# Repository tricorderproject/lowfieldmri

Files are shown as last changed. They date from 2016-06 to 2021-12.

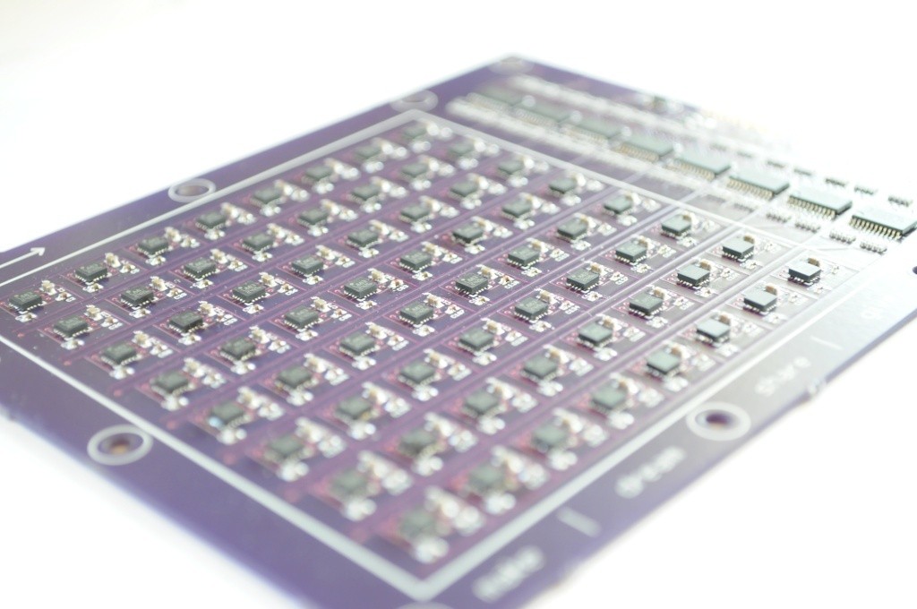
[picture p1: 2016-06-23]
hardware/magarray_v1/assembled_board1.jpg

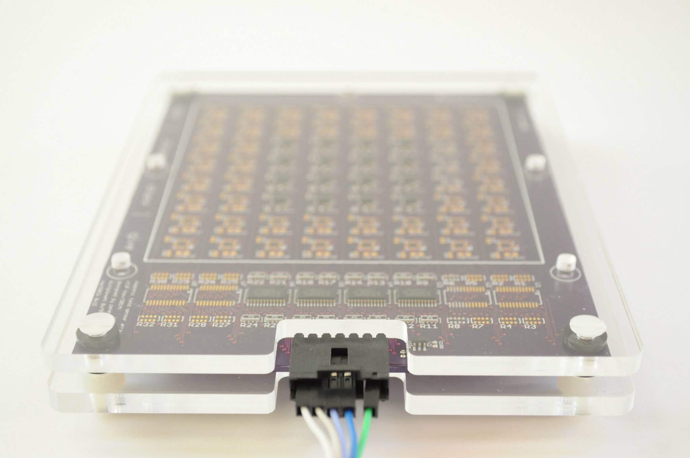
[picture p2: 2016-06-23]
hardware/magarray_v1/assembled_board2.jpg

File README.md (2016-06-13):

lowfieldmri
======

Experiments in Earth's field magnetic resonance imaging<br>

**DISCLAIMER OF WARRANTIES AND LIMITATION OF LIABILITY.**

UNLESS OTHERWISE SEPARATELY UNDERTAKEN BY THE LICENSOR, TO THE MAXIMUM EXTENT POSSIBLE, THE LICENSOR OFFERS THE LICENSED MATERIAL AS-IS AND AS-AVAILABLE, AND MAKES NO REPRESENTATIONS OR WARRANTIES OF ANY KIND CONCERNING THE LICENSED MATERIAL, WHETHER EXPRESS, IMPLIED, STATUTORY, OR OTHER. THIS INCLUDES, WITHOUT LIMITATION, WARRANTIES OF TITLE, MERCHANTABILITY, FITNESS FOR A PARTICULAR PURPOSE, NON-INFRINGEMENT, ABSENCE OF LATENT OR OTHER DEFECTS, ACCURACY, SAFETY, OR THE PRESENCE OR ABSENCE OF ERRORS, WHETHER OR NOT KNOWN OR DISCOVERABLE. WHERE DISCLAIMERS OF WARRANTIES ARE NOT ALLOWED IN FULL OR IN PART, THIS DISCLAIMER MAY NOT APPLY TO YOU.

TO THE EXTENT POSSIBLE, IN NO EVENT WILL THE LICENSOR BE LIABLE TO YOU ON ANY LEGAL THEORY (INCLUDING, WITHOUT LIMITATION, NEGLIGENCE) OR OTHERWISE FOR ANY DIRECT, SPECIAL, INDIRECT, INCIDENTAL, CONSEQUENTIAL, PUNITIVE, EXEMPLARY, OR OTHER LOSSES, COSTS, EXPENSES, OR DAMAGES ARISING OUT OF THIS PUBLIC LICENSE OR USE OF THE LICENSED MATERIAL, EVEN IF THE LICENSOR HAS BEEN ADVISED OF THE POSSIBILITY OF SUCH LOSSES, COSTS, EXPENSES, OR DAMAGES. WHERE A LIMITATION OF LIABILITY IS NOT ALLOWED IN FULL OR IN PART, THIS LIMITATION MAY NOT APPLY TO YOU.

THE DISCLAIMER OF WARRANTIES AND LIMITATION OF LIABILITY PROVIDED ABOVE SHALL BE INTERPRETED IN A MANNER THAT, TO THE EXTENT POSSIBLE, MOST CLOSELY APPROXIMATES AN ABSOLUTE DISCLAIMER AND WAIVER OF ALL LIABILITY.

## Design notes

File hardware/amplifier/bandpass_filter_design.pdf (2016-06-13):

## FilterPro Design Report

## Schematic

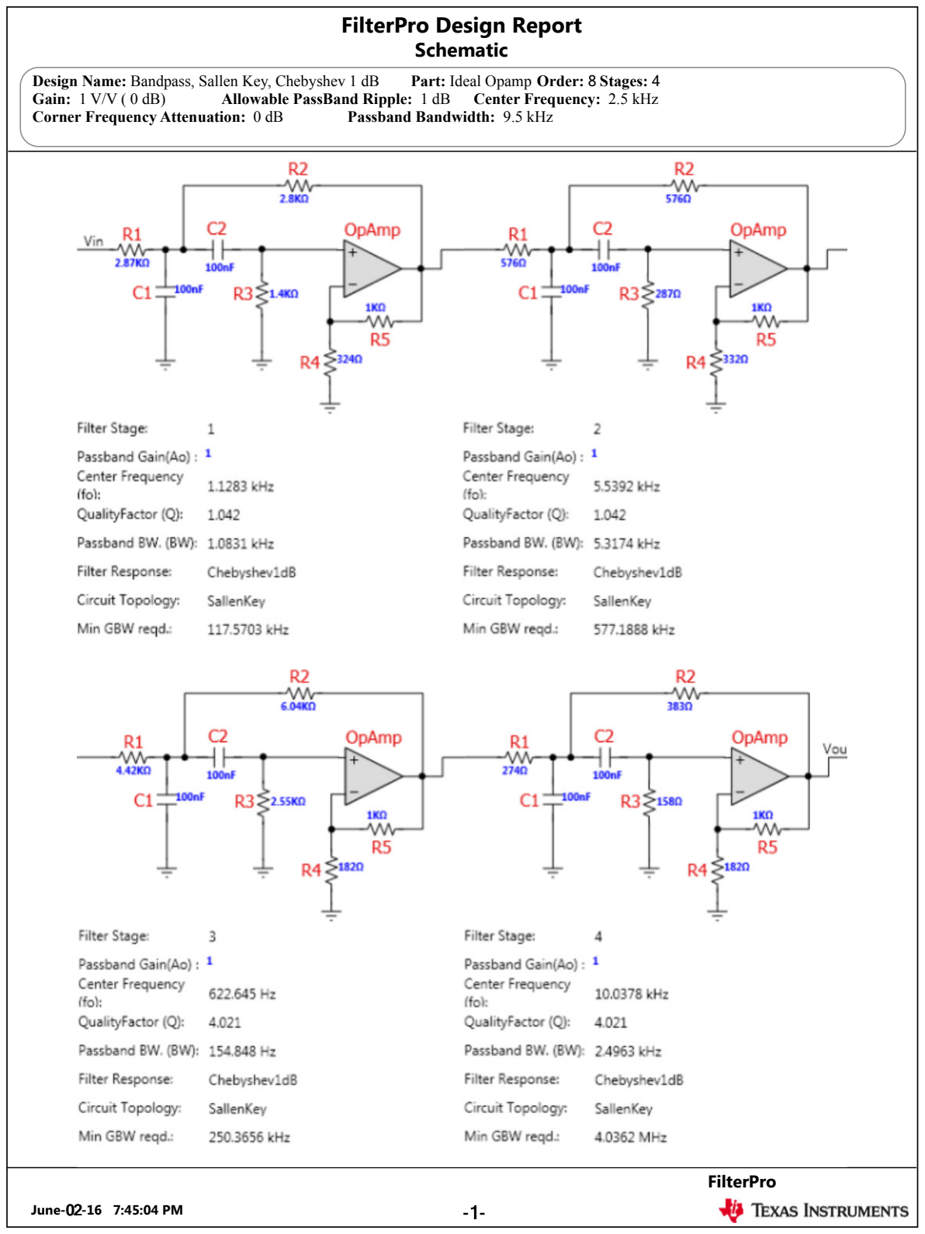
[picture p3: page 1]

Design Name: Bandpass, Sallen Key, Chebyshev 1 dB | Part: Ideal Opamp Order: 8 Stages: 4
Gain: 1 V/V ( 0 dB) | Allowable PassBand Ripple: 1 dB | Center Frequency: 2.5 kHz
Corner Frequency Attenuation: 0 dB | Passband Bandwidth: 9.5 kHz
June-02-16 7:45:04 PM | -1-

## FilterPro

## Frequency and Phase Responses

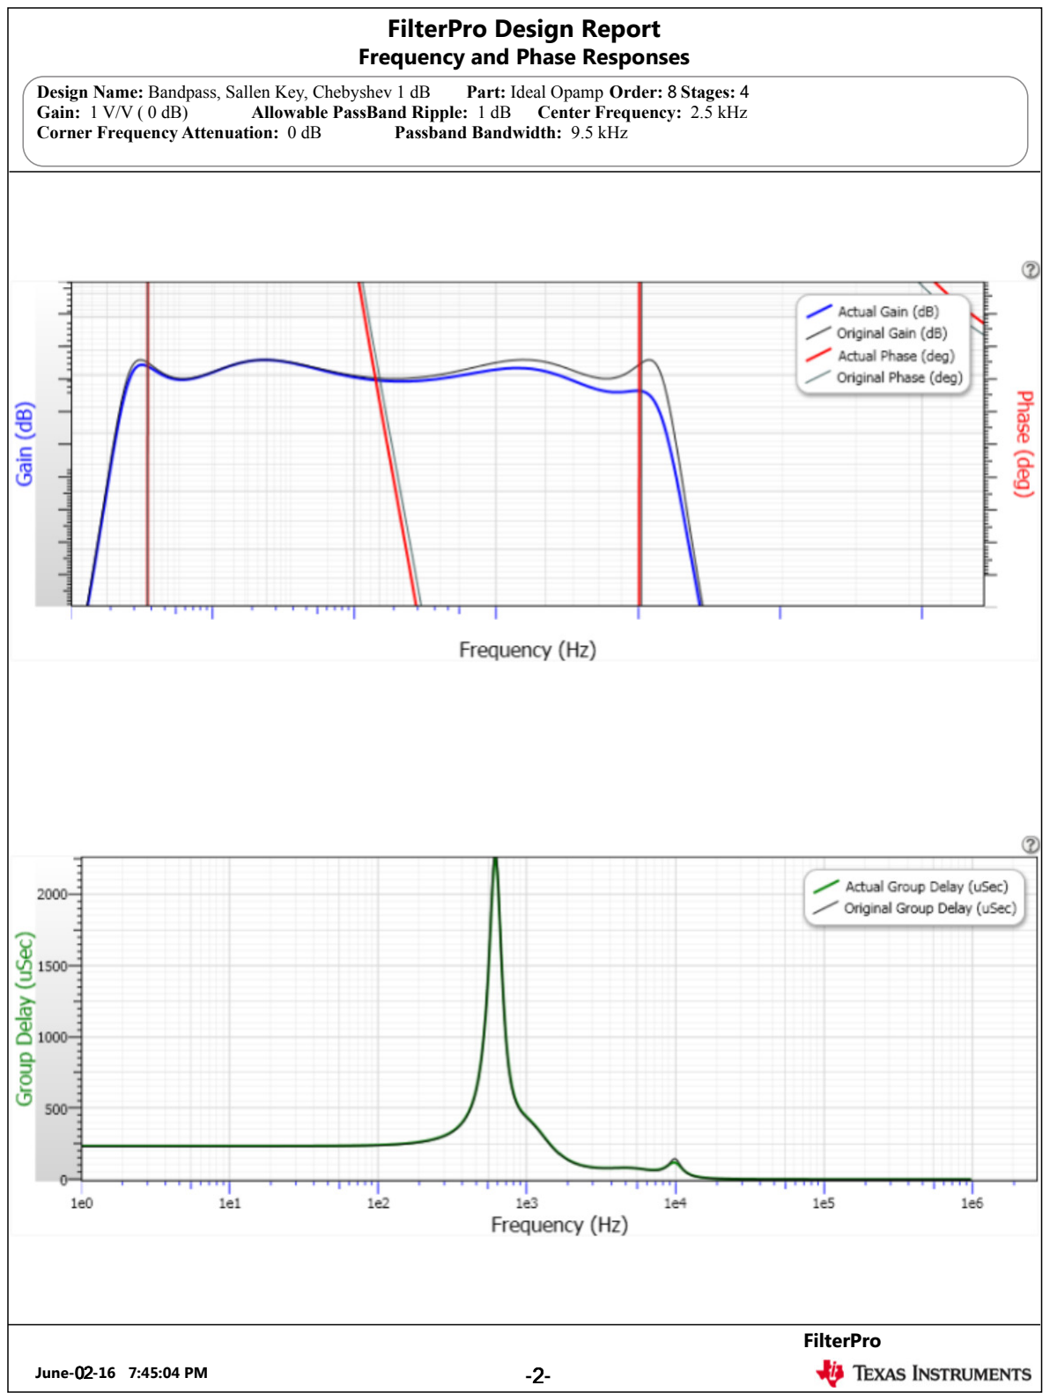
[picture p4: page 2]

Gain: 1 V/V ( 0 dB) | Allowable PassBand Ripple: 1 dB | Center Frequency: 2.5 kHz
Corner Frequency Attenuation: 0 dB | Passband Bandwidth: 9.5 kHz
June-02-16 7:45:04 PM | -2-

Gain: 1 V/V ( 0 dB) | Allowable PassBand Ripple: 1 dB | Center Frequency: 2.5 kHz
Corner Frequency Attenuation: 0 dB | Passband Bandwidth: 9.5 kHz

## Bill of Materials

June-02-16 7:45:04 PM | -3-
Element ID | Quantity | Part Number | Value | Tolerance | Description | Manufacturer
R1 (Stage 1) | 1 | Standard | 2.87KΩ | E96: 1% | Resistor
R2 (Stage 1) | 1 | Standard | 2.8KΩ | E96: 1% | Resistor
R3 (Stage 1) | 1 | Standard | 1.4KΩ | E96: 1% | Resistor
C1 (Stage 1) | 1 | Standard | 100nF | E96: 1% | Capacitor
C2 (Stage 1) | 1 | Standard | 100nF | E96: 1% | Capacitor
R4 (Stage 1) | 1 | Standard | 324Ω | E96: 1% | Resistor
R5 (Stage 1) | 1 | Standard | 1KΩ | E96: 1% | Resistor
OpAmp (Stage 1) | 1 | Standard | | | Ideal OpAmp
R1 (Stage 2) | 1 | Standard | 576Ω | E96: 1% | Resistor
R2 (Stage 2) | 1 | Standard | 576Ω | E96: 1% | Resistor
R3 (Stage 2) | 1 | Standard | 287Ω | E96: 1% | Resistor
C1 (Stage 2) | 1 | Standard | 100nF | E96: 1% | Capacitor
C2 (Stage 2) | 1 | Standard | 100nF | E96: 1% | Capacitor
R4 (Stage 2) | 1 | Standard | 332Ω | E96: 1% | Resistor
R5 (Stage 2) | 1 | Standard | 1KΩ | E96: 1% | Resistor
OpAmp (Stage 2) | 1 | Standard | | | Ideal OpAmp
R1 (Stage 3) | 1 | Standard | 4.42KΩ | E96: 1% | Resistor
R2 (Stage 3) | 1 | Standard | 6.04KΩ | E96: 1% | Resistor
R3 (Stage 3) | 1 | Standard | 2.55KΩ | E96: 1% | Resistor
C1 (Stage 3) | 1 | Standard | 100nF | E96: 1% | Capacitor
C2 (Stage 3) | 1 | Standard | 100nF | E96: 1% | Capacitor
R4 (Stage 3) | 1 | Standard | 182Ω | E96: 1% | Resistor
R5 (Stage 3) | 1 | Standard | 1KΩ | E96: 1% | Resistor
OpAmp (Stage 3) | 1 | Standard | | | Ideal OpAmp
R1 (Stage 4) | 1 | Standard | 274Ω | E96: 1% | Resistor
R2 (Stage 4) | 1 | Standard | 383Ω | E96: 1% | Resistor
R3 (Stage 4) | 1 | Standard | 158Ω | E96: 1% | Resistor
C1 (Stage 4) | 1 | Standard | 100nF | E96: 1% | Capacitor
C2 (Stage 4) | 1 | Standard | 100nF | E96: 1% | Capacitor
R4 (Stage 4) | 1 | Standard | 182Ω | E96: 1% | Resistor
R5 (Stage 4) | 1 | Standard | 1KΩ | E96: 1% | Resistor
OpAmp (Stage 4) | 1 | Standard | | | Ideal OpAmp

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

## Design Notes

June-02-16 7:45:04 PM | -4-

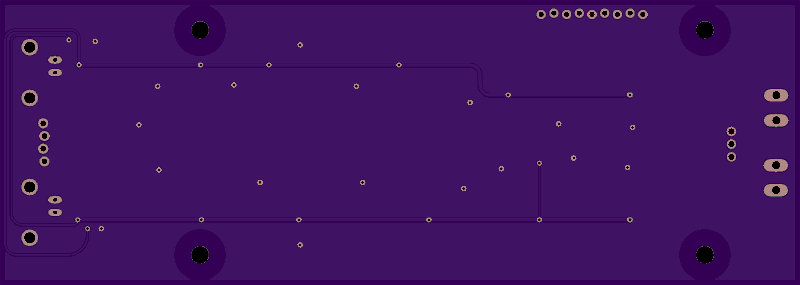
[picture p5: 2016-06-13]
hardware/amplifier/amplifier4c_bottom.png

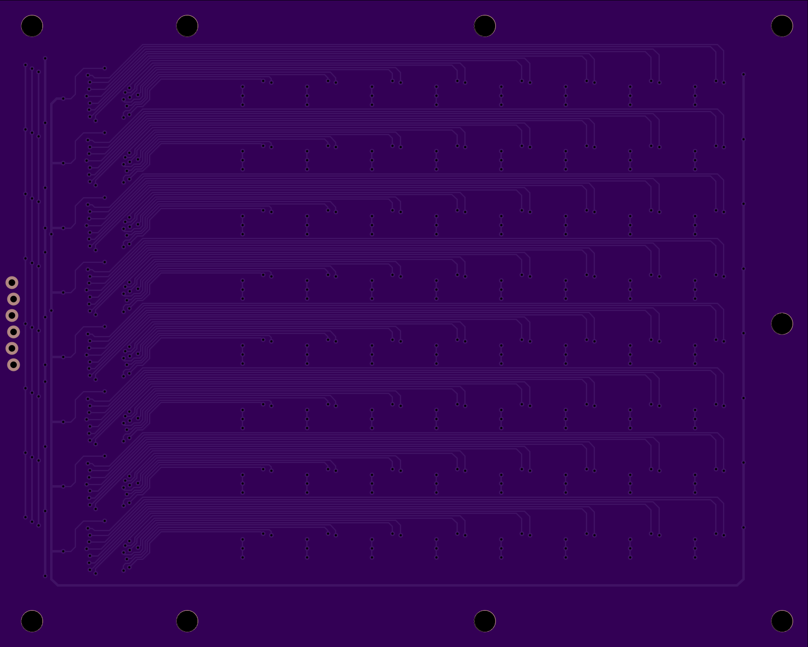
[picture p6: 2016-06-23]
hardware/magarray_v1/board_bottom.png

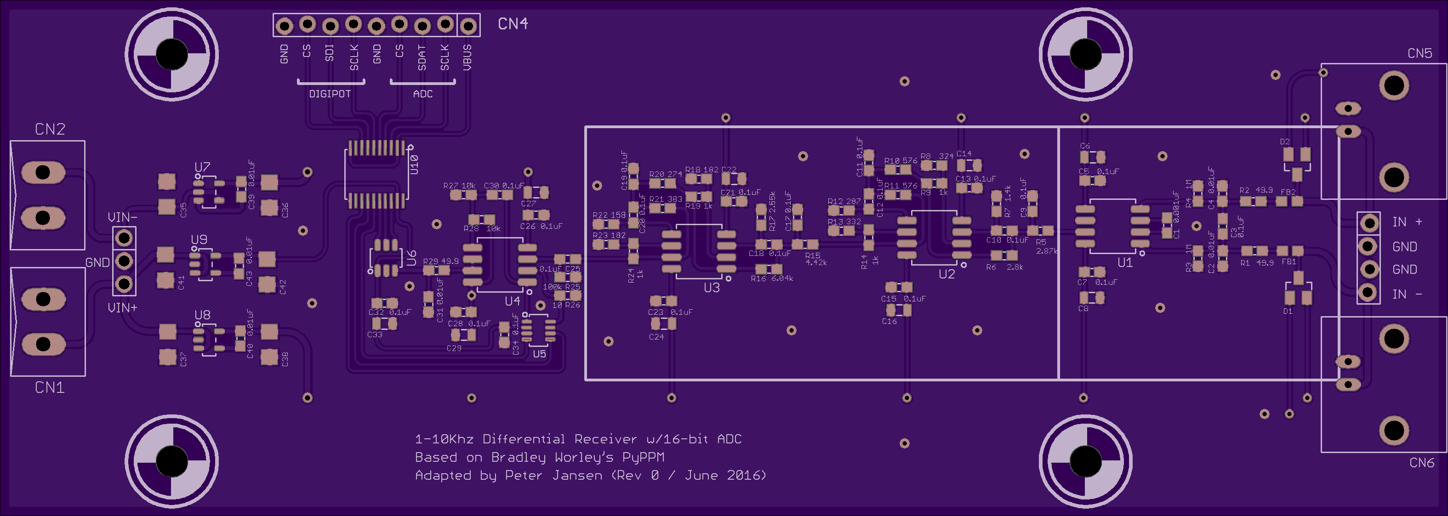
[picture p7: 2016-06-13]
hardware/amplifier/amplifier4c_top.png

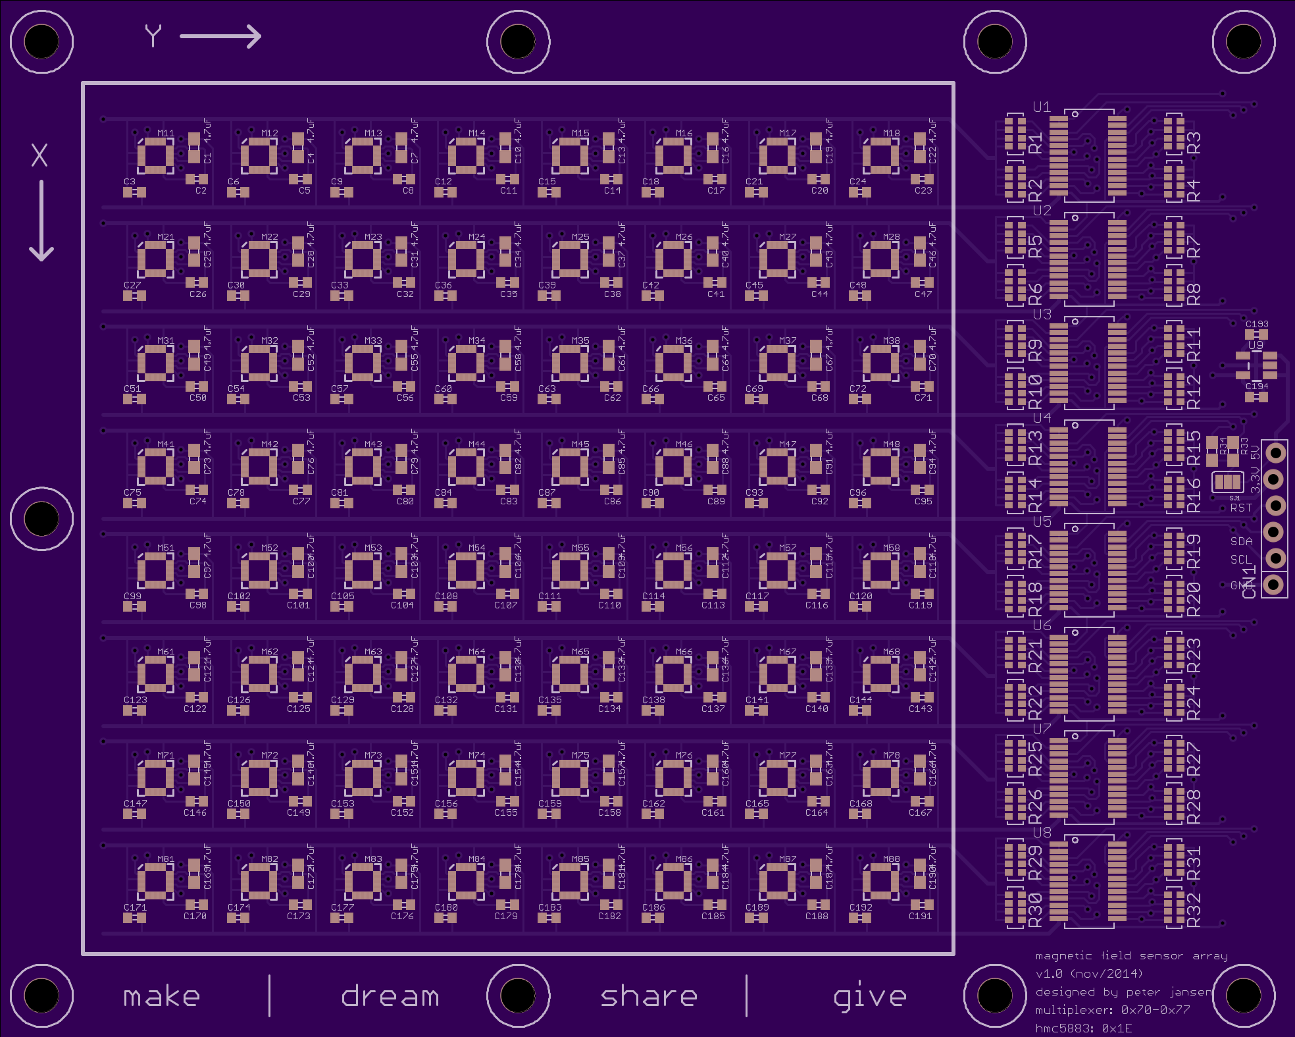
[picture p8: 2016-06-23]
hardware/magarray_v1/board_top.png

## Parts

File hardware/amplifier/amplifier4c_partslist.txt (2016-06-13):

Partlist

Exported from amplifier4c.sch at 12/06/2016 5:14:38 PM

EAGLE Version 6.5.0 Copyright (c) 1988-2013 CadSoft

Assembly variant: 

Part     Value               Device              Package            Library             Sheet

C1       0.001uF             CAP0603             0603               lowfieldmri         1
C2       0.01uF              CAP0603             0603               lowfieldmri         1
C3       0.1uF               CAP0603             0603               lowfieldmri         1
C4       0.01uF              CAP0603             0603               lowfieldmri         1
C5       0.1uF               CAP0603             0603               lowfieldmri         1
C6       10uF                CAP0805             0805               lowfieldmri         1
C7       0.1uF               CAP0603             0603               lowfieldmri         1
C8       10uF                CAP0805             0805               lowfieldmri         1
C9       0.1uF               CAP0603             0603               lowfieldmri         1
C10      0.1uF               CAP0603             0603               lowfieldmri         1
C11      0.1uF               CAP0603             0603               lowfieldmri         1
C12      0.1uF               CAP0603             0603               lowfieldmri         1
C13      0.1uF               CAP0603             0603               lowfieldmri         1
C14      10uF                CAP0805             0805               lowfieldmri         1
C15      0.1uF               CAP0603             0603               lowfieldmri         1
C16      10uF                CAP0805             0805               lowfieldmri         1
C17      0.1uF               CAP0603             0603               lowfieldmri         1
C18      0.1uF               CAP0603             0603               lowfieldmri         1
C19      0.1uF               CAP0603             0603               lowfieldmri         1
C20      0.1uF               CAP0603             0603               lowfieldmri         1
C21      0.1uF               CAP0603             0603               lowfieldmri         1
C22      10uF                CAP0805             0805               lowfieldmri         1
C23      0.1uF               CAP0603             0603               lowfieldmri         1
C24      10uF                CAP0805             0805               lowfieldmri         1
C25      0.1uF               CAP0603             0603               lowfieldmri         1
C26      0.1uF               CAP0603             0603               lowfieldmri         1
C27      10uF                CAP0805             0805               lowfieldmri         1
C28      0.1uF               CAP0603             0603               lowfieldmri         1
C29      10uF                CAP0805             0805               lowfieldmri         1
C30      0.1uF               CAP0603             0603               lowfieldmri         1
C31      0.01uF              CAP0603             0603               lowfieldmri         1
C32      0.1uF               CAP0603             0603               lowfieldmri         1
C33      10uF                CAP0805             0805               lowfieldmri         1
C34      0.1uF               CAP0603             0603               lowfieldmri         1
C35      22uF                CAP1206             1206               SparkFun-Capacitors 1
C36      22uF                CAP1206             1206               SparkFun-Capacitors 1
C37      22uF                CAP1206             1206               SparkFun-Capacitors 1
C38      22uF                CAP1206             1206               SparkFun-Capacitors 1
C39      0.01uF              CAP0603             0603               lowfieldmri         1
C40      0.01uF              CAP0603             0603               lowfieldmri         1
C41      22uF                CAP1206             1206               SparkFun-Capacitors 1
C42      22uF                CAP1206             1206               SparkFun-Capacitors 1
C43      0.01uF              CAP0603             0603               lowfieldmri         1
CN1      SCREWTERMINAL-2PIN  SCREWTERMINAL-2PIN  SCREWTERMINAL-2PIN openct              1
CN2      SCREWTERMINAL-2PIN  SCREWTERMINAL-2PIN  SCREWTERMINAL-2PIN openct              1
CN3      1X03                1X03                1X03               openct              1
CN4      1X09                1X09                1X09               lowfieldmri         1
CN5      BNCPTH              BNCPTH              BNC                SparkFun-Connectors 1
CN6      BNCPTH              BNCPTH              BNC                SparkFun-Connectors 1
CN7      1X04                1X04                1X04               lowfieldmri         1
D1       BAV199              BAV199              SOT23              diode               1
D2       BAV199              BAV199              SOT23              diode               1
FB1      FB                  FB                  0603               SparkFun-Passives   1
FB2      FB                  FB                  0603               SparkFun-Passives   1
R1       49.9                RESISTOR0603        0603               lowfieldmri         1
R2       49.9                RESISTOR0603        0603               lowfieldmri         1
R3       1M                  RESISTOR0603        0603               lowfieldmri         1
R4       1M                  RESISTOR0603        0603               lowfieldmri         1
R5       2.87k               RESISTOR0603        0603               lowfieldmri         1
R6       2.8k                RESISTOR0603        0603               lowfieldmri         1
R7       1.4k                RESISTOR0603        0603               lowfieldmri         1
R8       324                 RESISTOR0603        0603               lowfieldmri         1
R9       1k                  RESISTOR0603        0603               lowfieldmri         1
R10      576                 RESISTOR0603        0603               lowfieldmri         1
R11      576                 RESISTOR0603        0603               lowfieldmri         1
R12      287                 RESISTOR0603        0603               lowfieldmri         1
R13      332                 RESISTOR0603        0603               lowfieldmri         1
R14      1k                  RESISTOR0603        0603               lowfieldmri         1
R15      4.42k               RESISTOR0603        0603               lowfieldmri         1
R16      6.04k               RESISTOR0603        0603               lowfieldmri         1
R17      2.55k               RESISTOR0603        0603               lowfieldmri         1
R18      182                 RESISTOR0603        0603               lowfieldmri         1
R19      1k                  RESISTOR0603        0603               lowfieldmri         1
R20      274                 RESISTOR0603        0603               lowfieldmri         1
R21      383                 RESISTOR0603        0603               lowfieldmri         1
R22      158                 RESISTOR0603        0603               lowfieldmri         1
R23      182                 RESISTOR0603        0603               lowfieldmri         1
R24      1k                  RESISTOR0603        0603               lowfieldmri         1
R25      100k                RESISTOR0603        0603               lowfieldmri         1
R26      10                  RESISTOR0603        0603               lowfieldmri         1
R27      10k                 RESISTOR0603        0603               lowfieldmri         1
R28      10k                 RESISTOR0603        0603               lowfieldmri         1
R29      49.9                RESISTOR0603        0603               lowfieldmri         1
U1       OPAMP-AD8428        OPAMP-AD8428        SOIC-8             lowfieldmri         1
U2       OPAMP-OP262         OPAMP-OP262         SOIC-8             lowfieldmri         1
U3       OPAMP-OP262         OPAMP-OP262         SOIC-8             lowfieldmri         1
U4       OPAMP-OP262         OPAMP-OP262         SOIC-8             lowfieldmri         1
U5       5k                  AD5160              SOT-23-8           lowfieldmri         1
U6       ADC-AD7680          ADC-AD7680          SOT-23-6L          lowfieldmri         1
U7       LT1964-5            REG-LT1964-X        SOT-23-5L          lowfieldmri         1
U8       LT1761-5            REG-LT1761-X        SOT-23-5L          lowfieldmri         1
U9       LT1761-5            REG-LT1761-X        SOT-23-5L          lowfieldmri         1
U10      TRANSLATOR-TXS0108E TRANSLATOR-TXS0108E TSSOP-20           arducorder-mini     1

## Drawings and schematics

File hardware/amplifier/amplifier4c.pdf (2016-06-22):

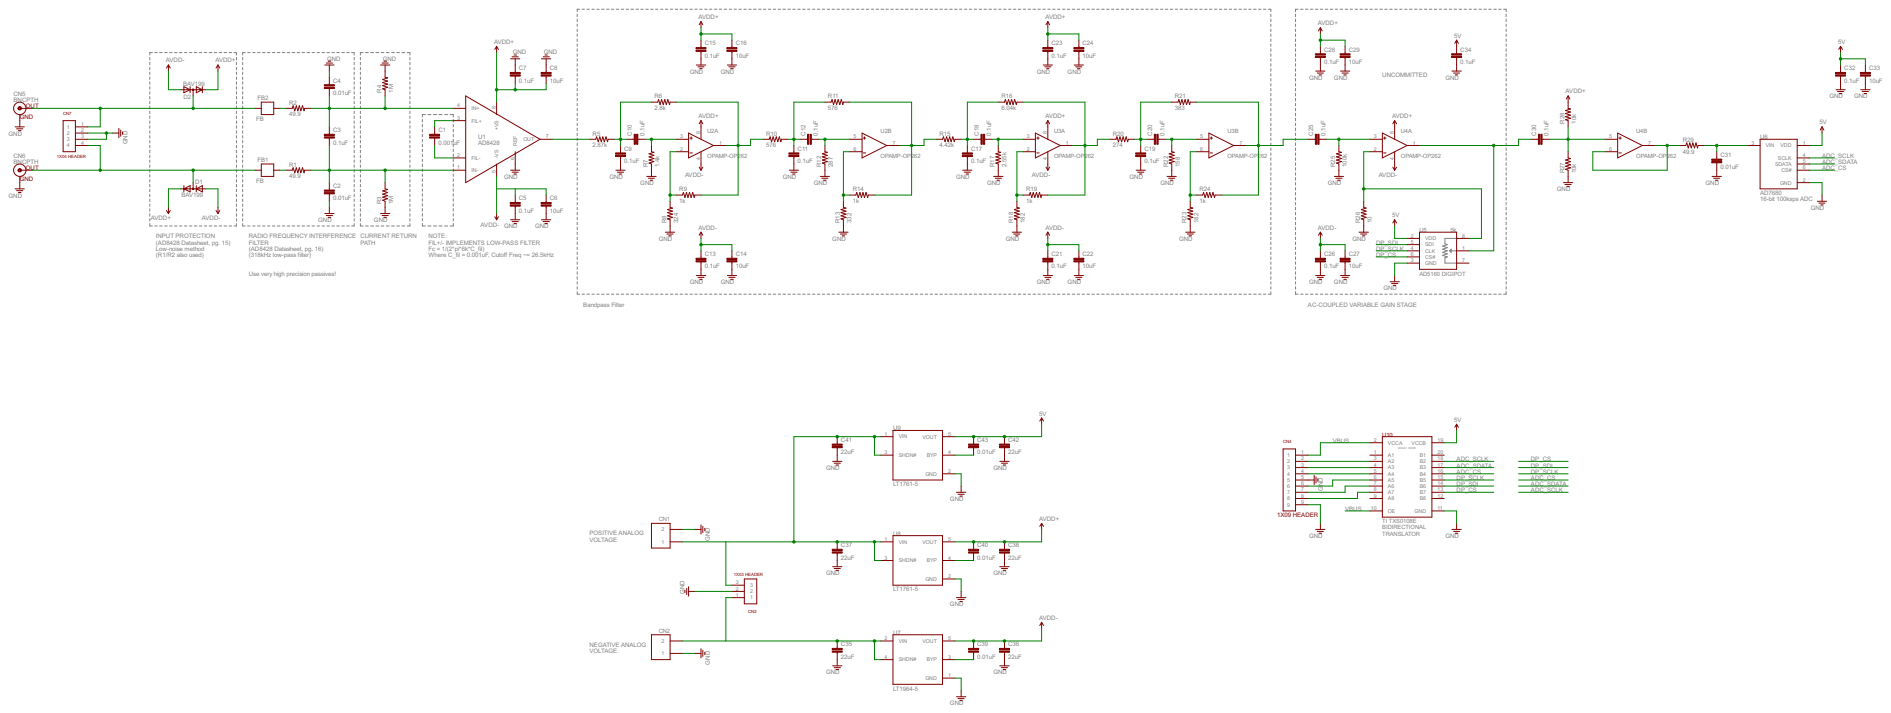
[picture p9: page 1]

1 2 3 4 | 3 2 0.001uF | FIL- 2

FIL+/- IMPLEMENTS LOW-PASS FILTER
Fc = 1/(2*pi*6k*C_fil) Where C_fil = 0.001uF, Cutoff Freq ~= 26.5kHz

AC-COUPLED VARIABLE GAIN STAGE

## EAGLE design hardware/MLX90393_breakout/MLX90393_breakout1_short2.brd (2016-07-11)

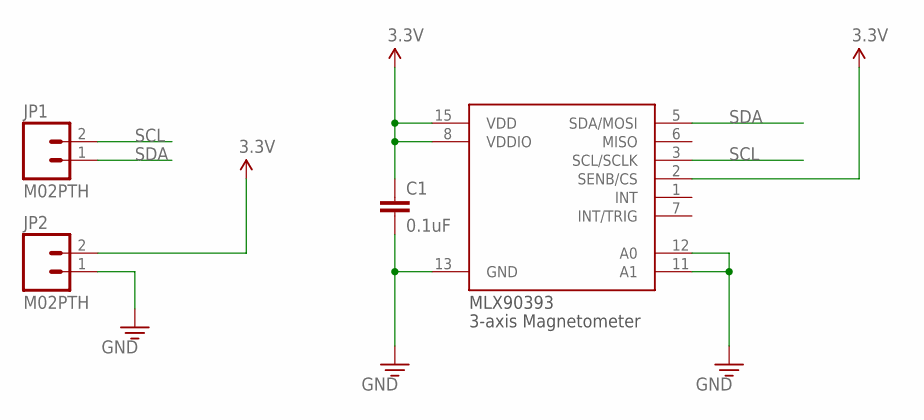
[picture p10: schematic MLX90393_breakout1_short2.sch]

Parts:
C1: 0.1uF; 0603
JP1, JP2: M02PTH; 1X02
U$1: MLX90393; 16-QFN

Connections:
3.3V: C1.1, JP2.2, U$1.2 (SENB/CS), U$1.8 (VDDIO), U$1.15 (VDD)
GND: C1.2, JP2.1, U$1.11 (A1), U$1.12 (A0), U$1.13 (GND)
SCL: JP1.2, U$1.3 (SCL/SCLK)
SDA: JP1.1, U$1.5 (SDA/MOSI)

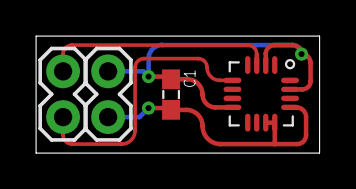
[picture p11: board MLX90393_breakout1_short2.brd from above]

Board: 2 copper layers, 15.8 x 6.5 mm, 4 parts (0 on the bottom side), 4 nets.

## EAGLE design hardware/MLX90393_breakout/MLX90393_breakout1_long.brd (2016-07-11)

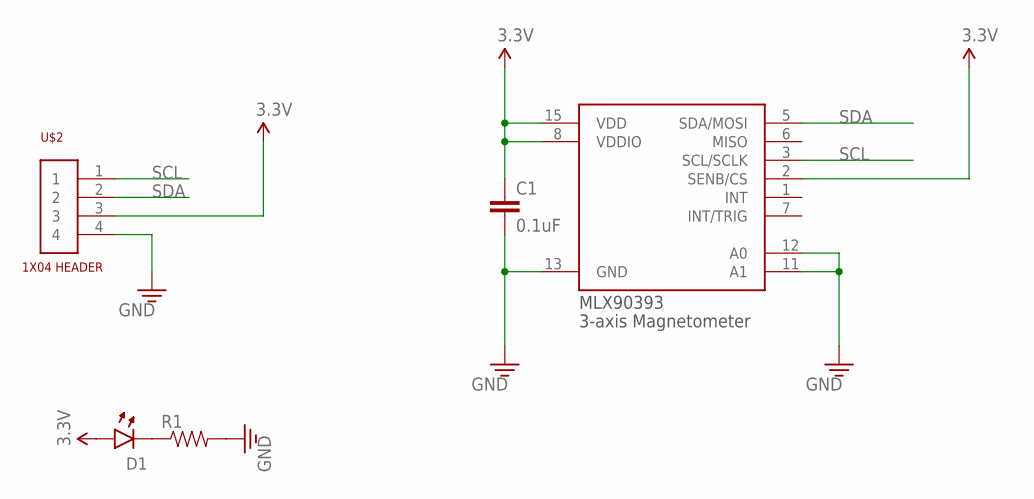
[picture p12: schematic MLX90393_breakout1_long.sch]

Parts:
C1: 0.1uF; 0603
D1: 0605-LED; 0603-LED
R1: RESISTOR0603; 0603
U$1: MLX90393; 16-QFN
U$2: 1X04

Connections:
3.3V: C1.1, D1.ANODE, U$1.2 (SENB/CS), U$1.8 (VDDIO), U$1.15 (VDD), U$2.3
GND: C1.2, R1.2, U$1.11 (A1), U$1.12 (A0), U$1.13 (GND), U$2.4
unnamed: D1.CATHODE, R1.1
SCL: U$1.3 (SCL/SCLK), U$2.1
SDA: U$1.5 (SDA/MOSI), U$2.2

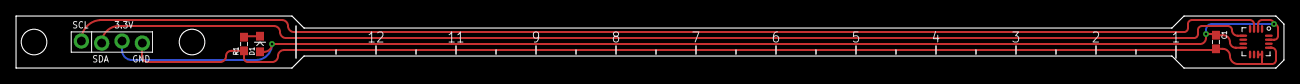
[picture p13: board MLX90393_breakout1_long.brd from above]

Board: 2 copper layers, 158.5 x 6.5 mm, 5 parts (0 on the bottom side), 5 nets.

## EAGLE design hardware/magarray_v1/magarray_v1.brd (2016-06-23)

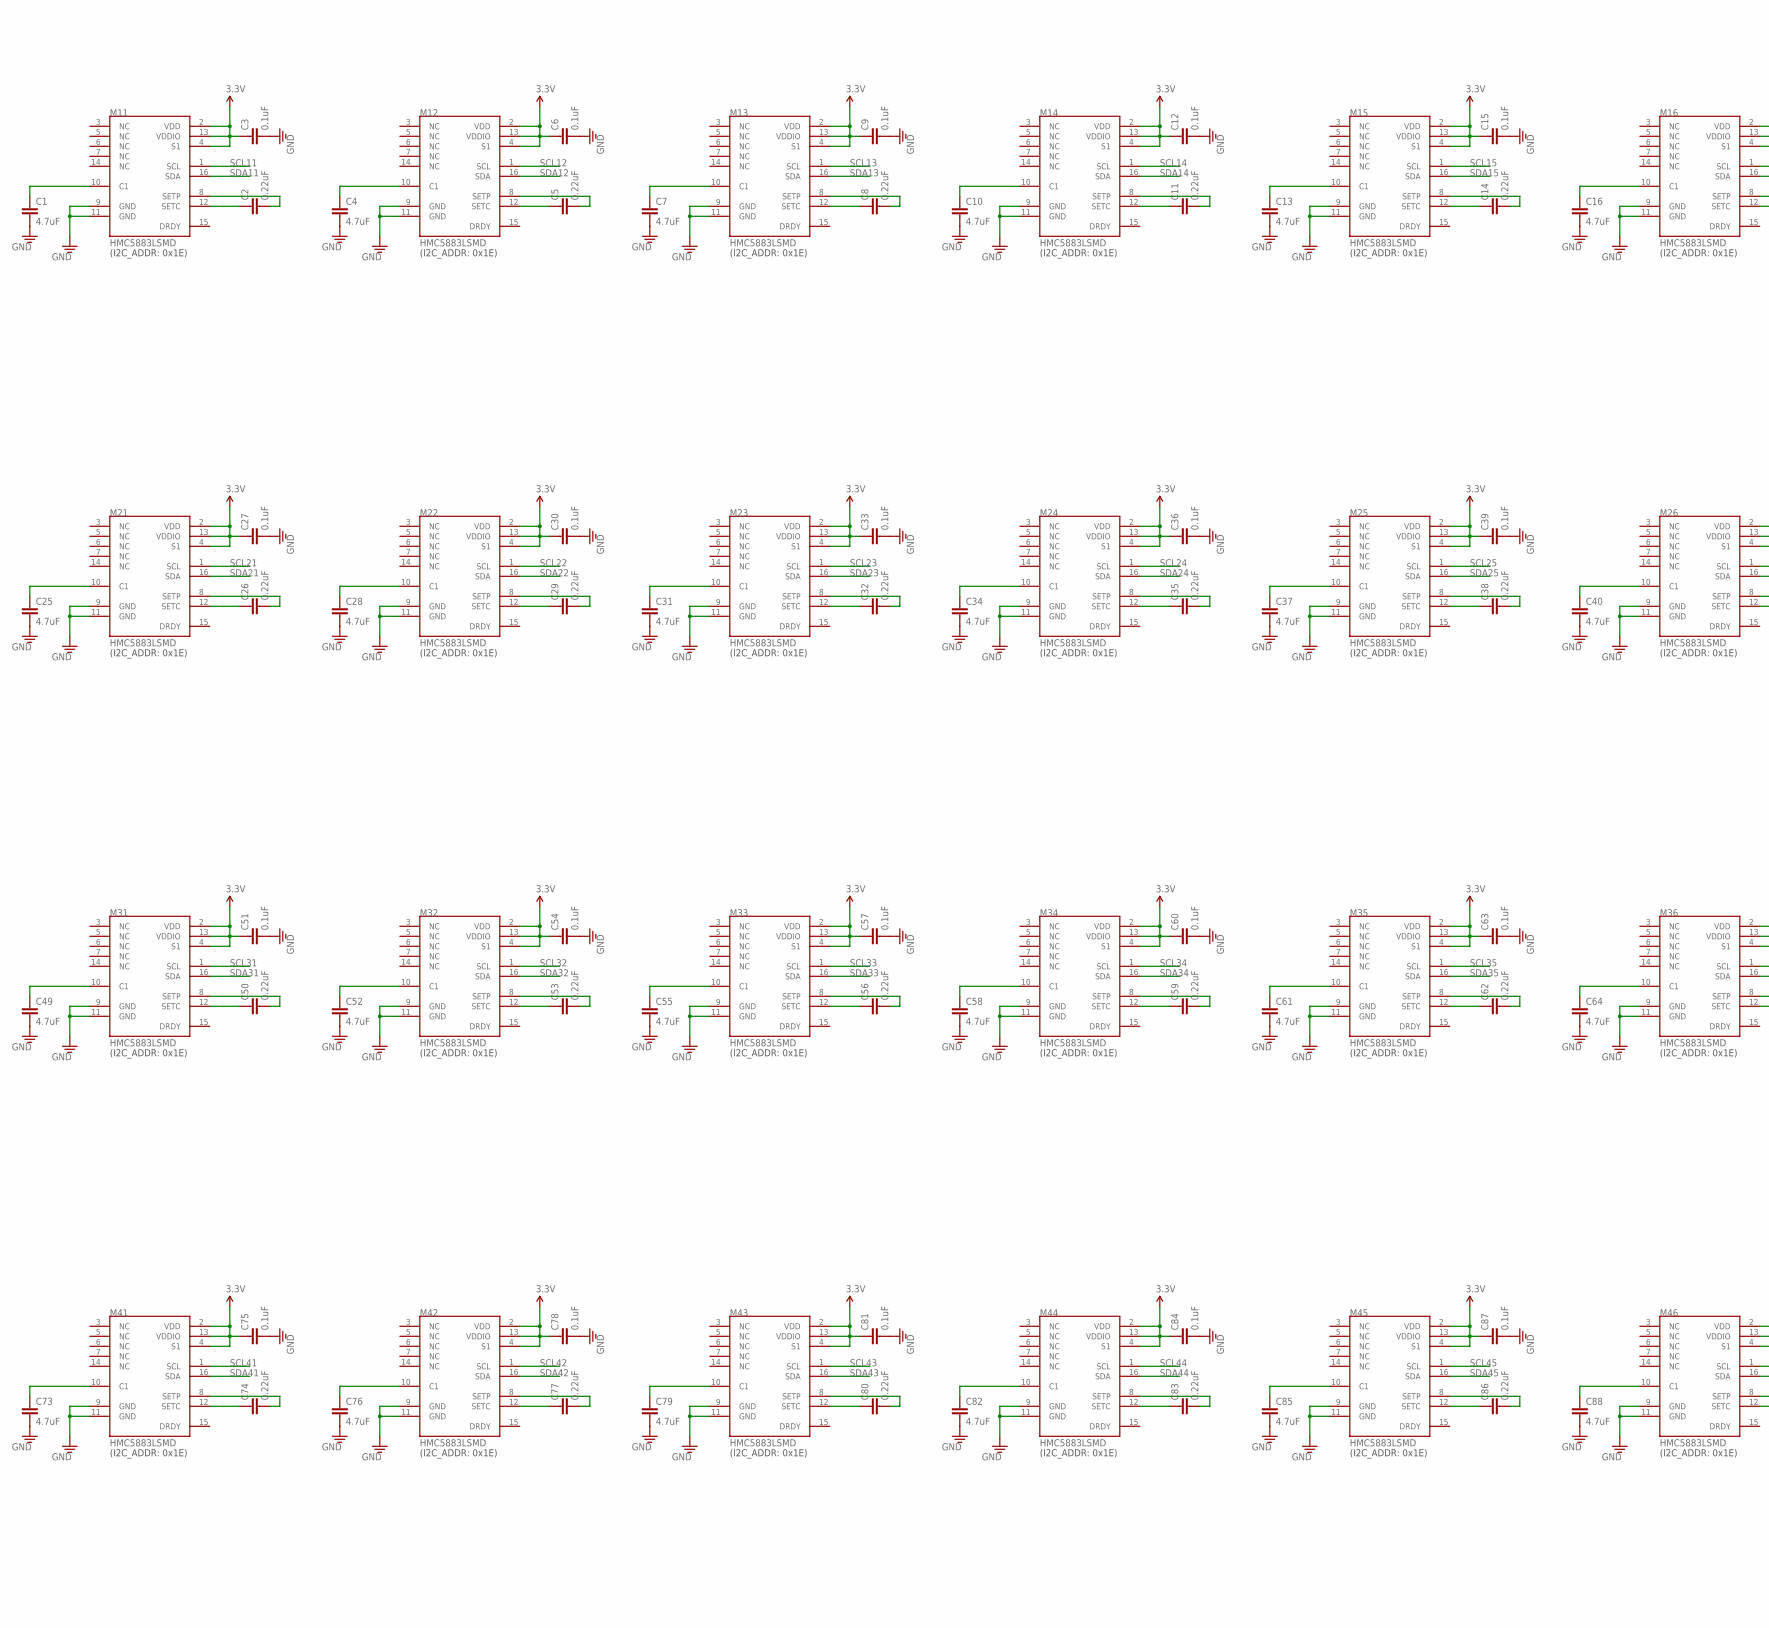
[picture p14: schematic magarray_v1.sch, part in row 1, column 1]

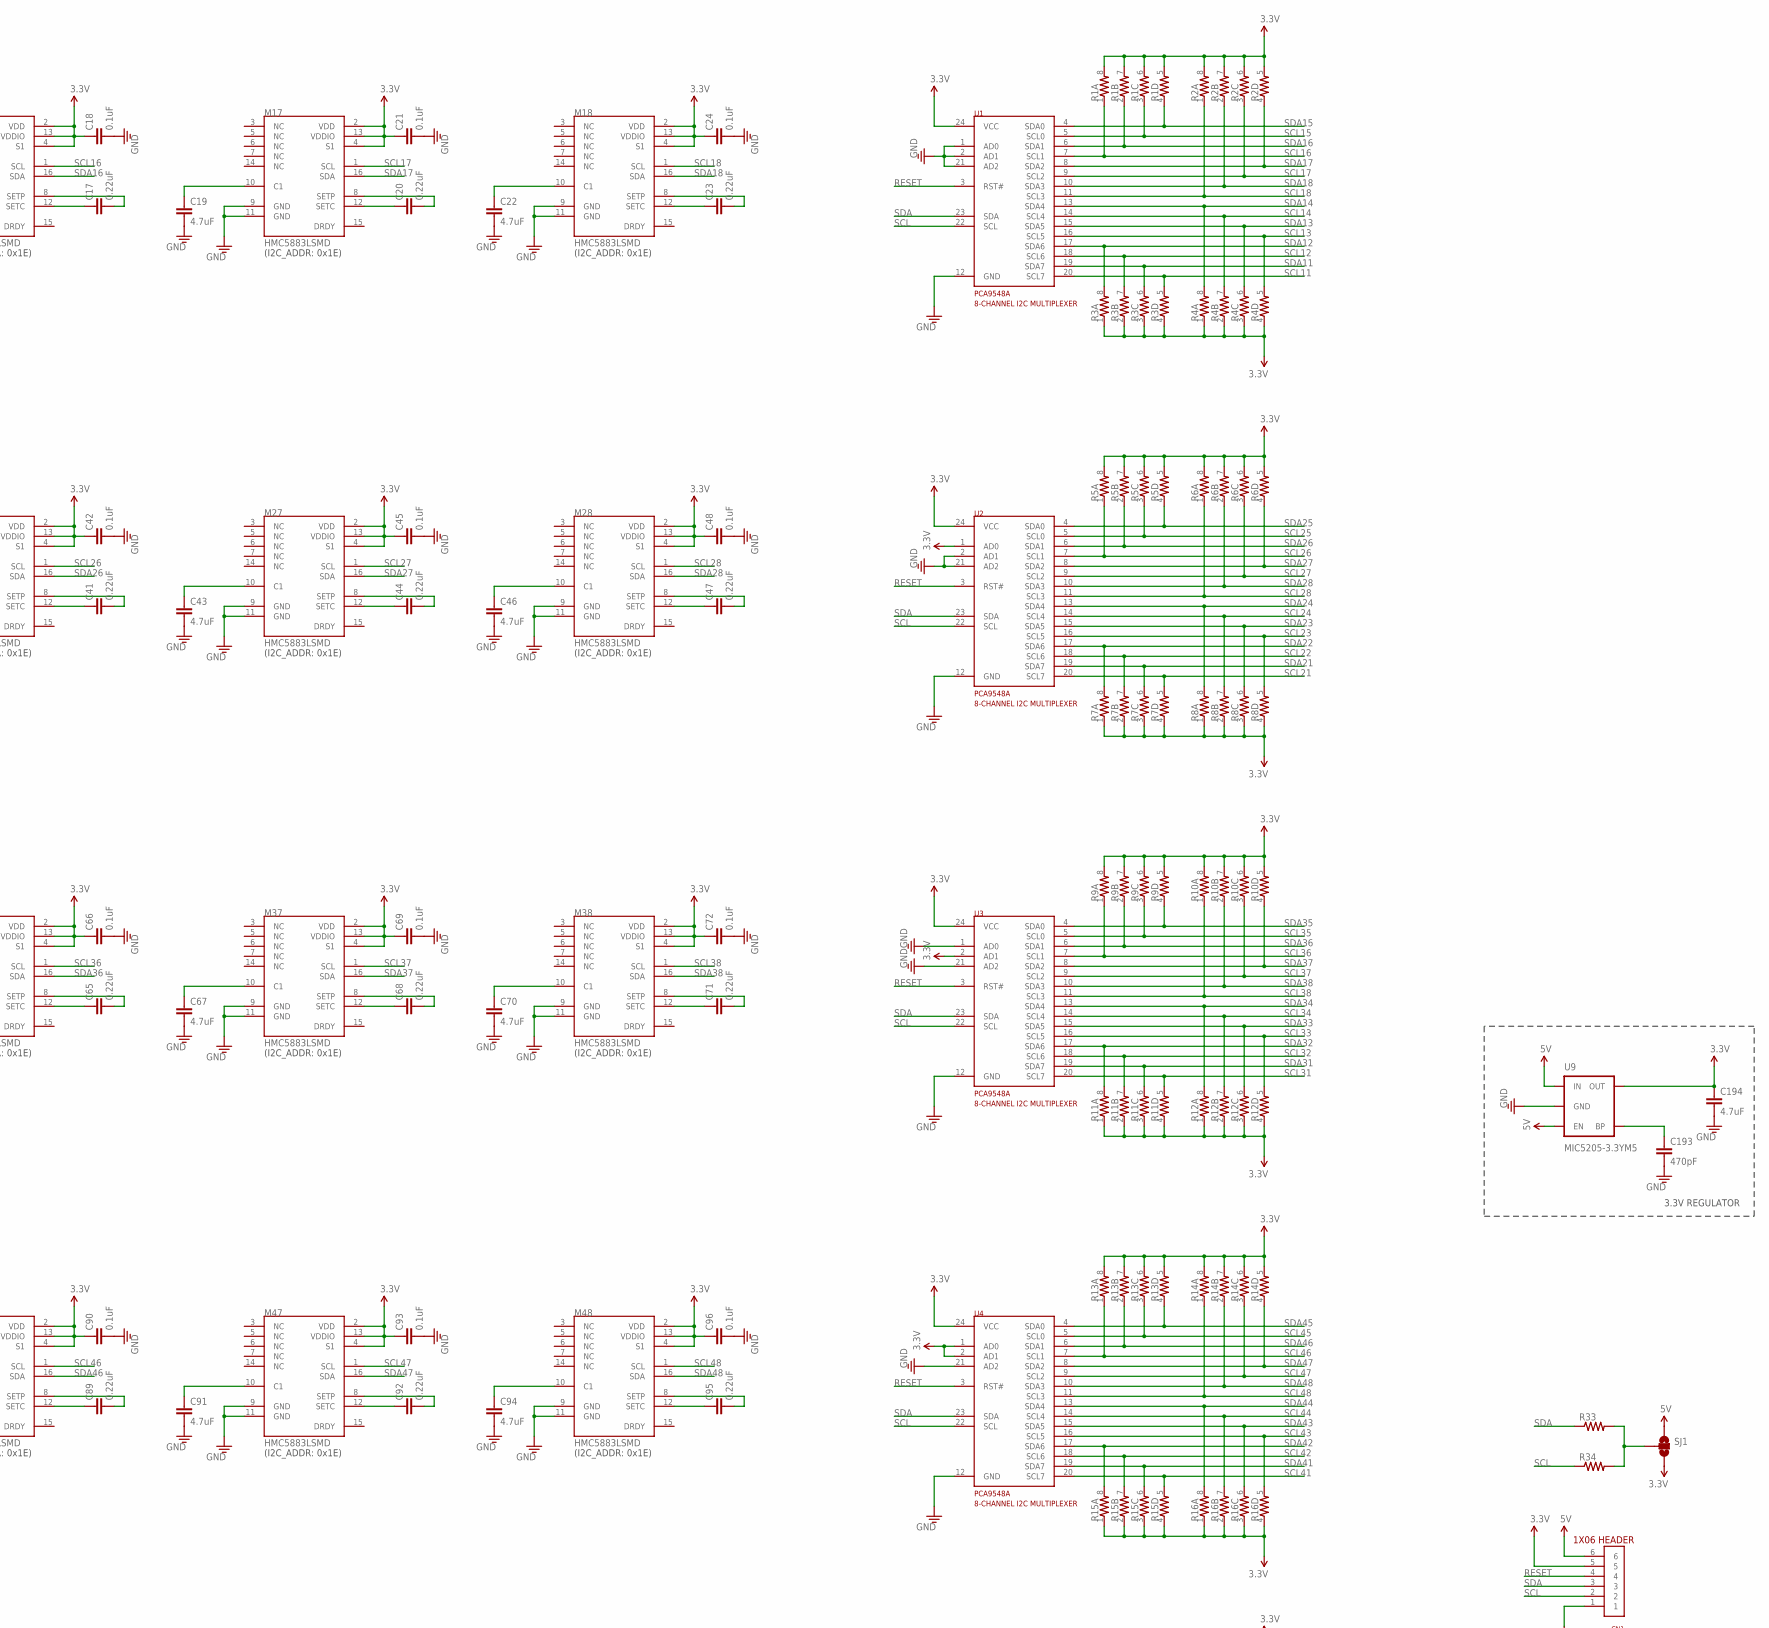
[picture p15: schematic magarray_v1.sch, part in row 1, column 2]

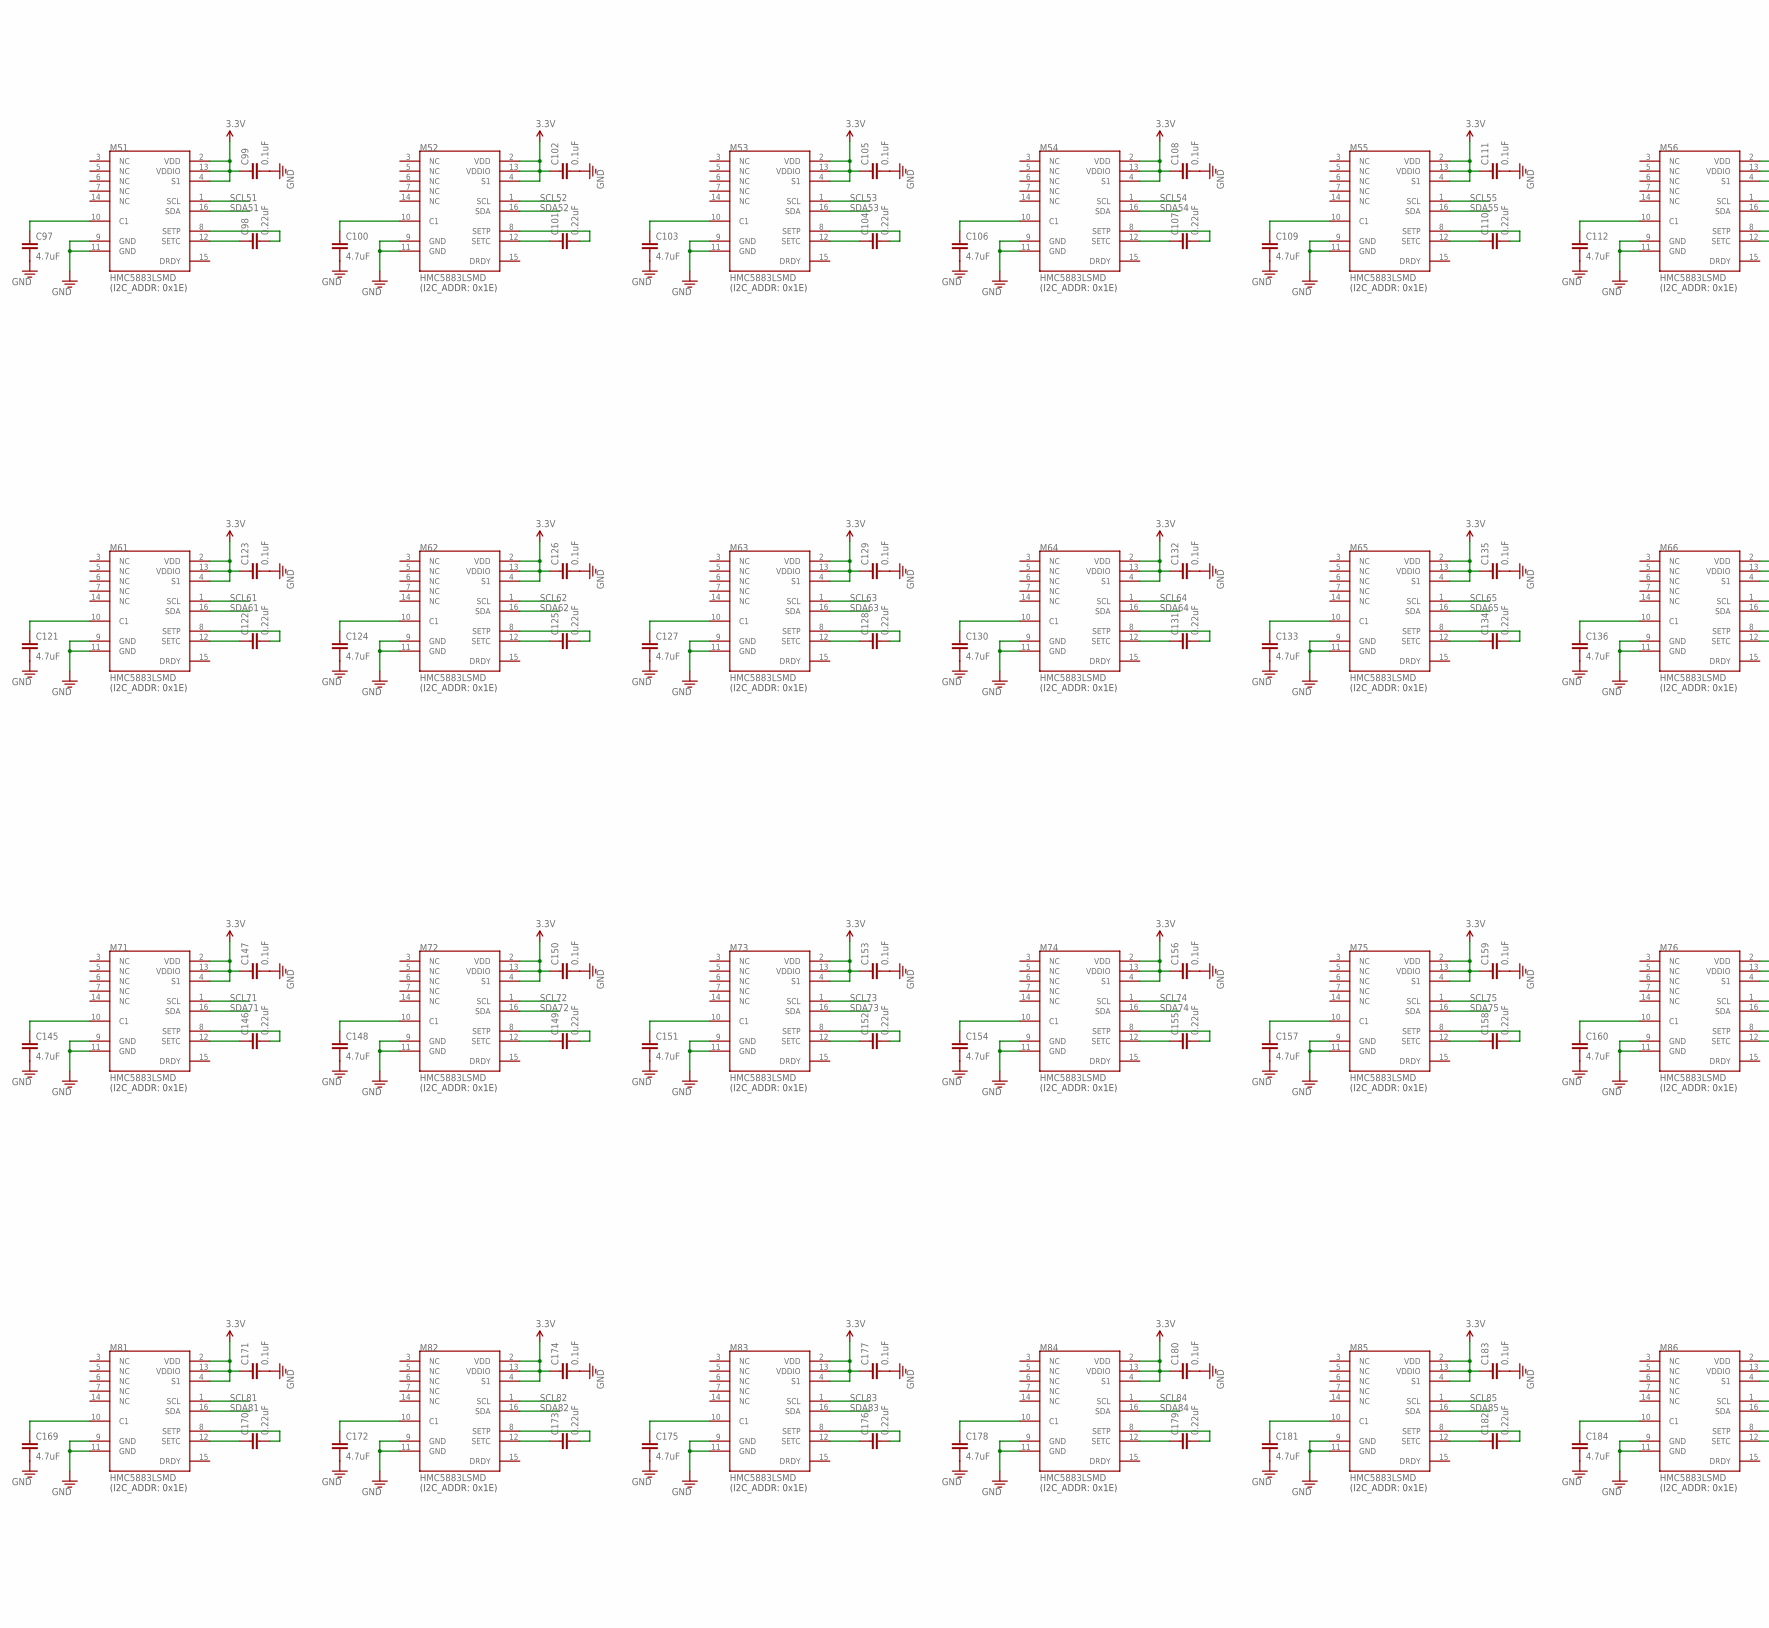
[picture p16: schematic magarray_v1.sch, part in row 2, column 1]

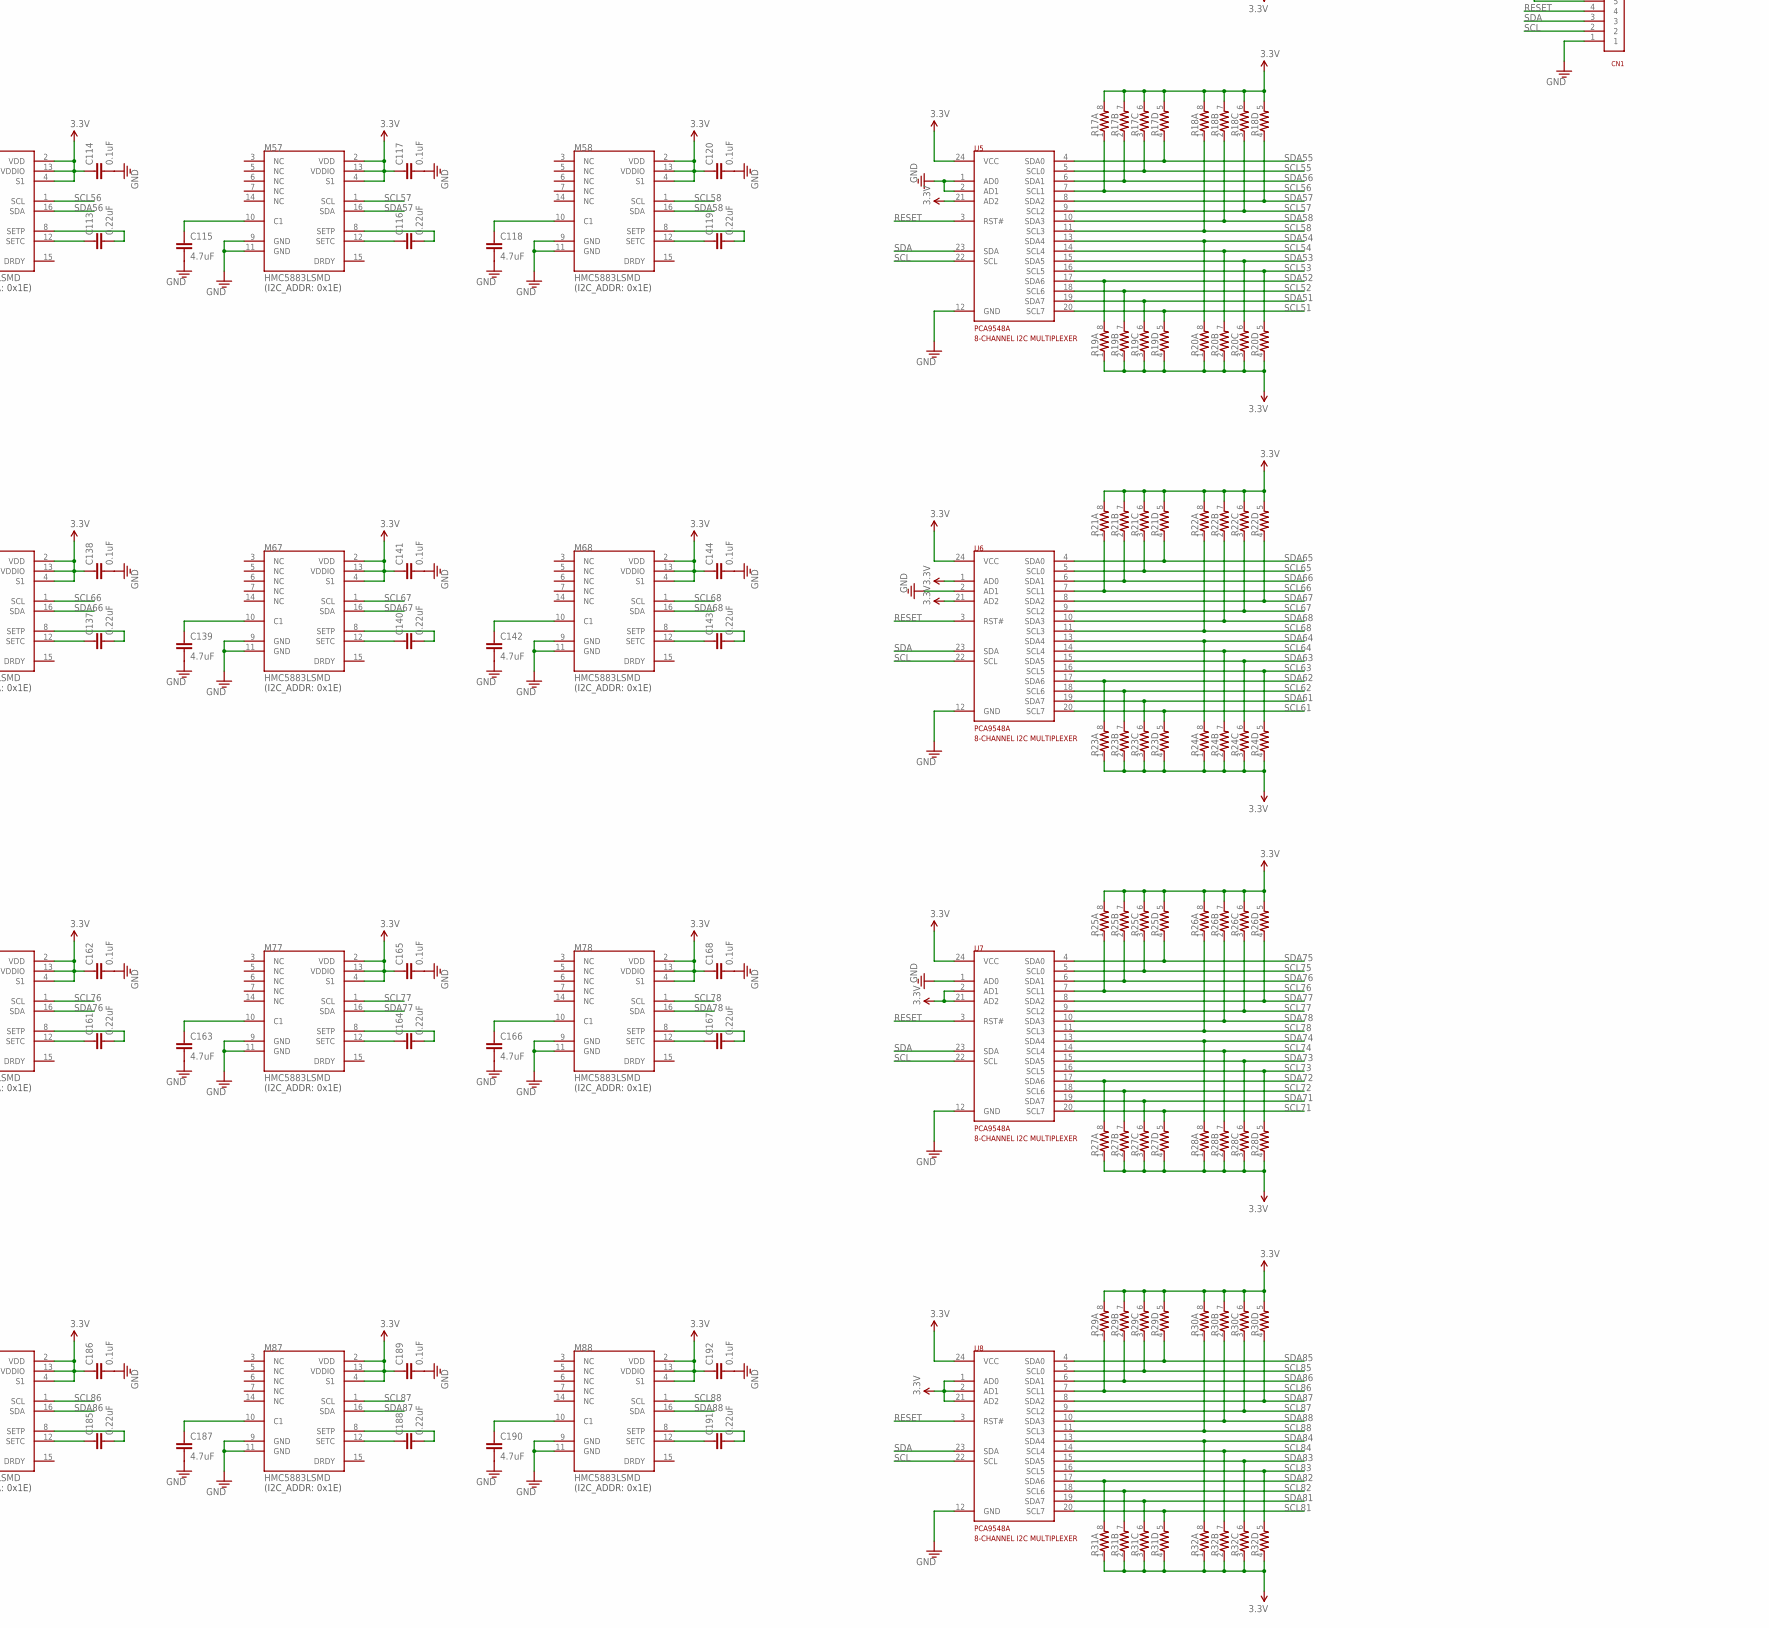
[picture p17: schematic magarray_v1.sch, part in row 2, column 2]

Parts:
C1, C4, C7, C10, C13, C16, C19, C22, C25, C28, C31, C34, C37, C40, C43, C46, C49, C52, C55, C58, C61, C64, C67, C70, C73, C76, C79, C82, C85, C88, C91, C94, C97, C100, C103, C106, C109, C112, C115, C118, C121, C124, C127, C130, C133, C136, C139, C142, C145, C148, C151, C154, C157, C160, C163, C166, C169, C172, C175, C178, C181, C184, C187, C190: 4.7uF; 0603
C2, C5, C8, C11, C14, C17, C20, C23, C26, C29, C32, C35, C38, C41, C44, C47, C50, C53, C56, C59, C62, C65, C68, C71, C74, C77, C80, C83, C86, C89, C92, C95, C98, C101, C104, C107, C110, C113, C116, C119, C122, C125, C128, C131, C134, C137, C140, C143, C146, C149, C152, C155, C158, C161, C164, C167, C170, C173, C176, C179, C182, C185, C188, C191: 0.22uF; C0402
C3, C6, C9, C12, C15, C18, C21, C24, C27, C30, C33, C36, C39, C42, C45, C48, C51, C54, C57, C60, C63, C66, C69, C72, C75, C78, C81, C84, C87, C90, C93, C96, C99, C102, C105, C108, C111, C114, C117, C120, C123, C126, C129, C132, C135, C138, C141, C144, C147, C150, C153, C156, C159, C162, C165, C168, C171, C174, C177, C180, C183, C186, C189, C192: 0.1uF; C0402
C193: 470pF; C0402
C194: 4.7uF; C0402
CN1: 1X06
M11, M12, M13, M14, M15, M16, M17, M18, M21, M22, M23, M24, M25, M26, M27, M28, M31, M32, M33, M34, M35, M36, M37, M38, M41, M42, M43, M44, M45, M46, M47, M48, M51, M52, M53, M54, M55, M56, M57, M58, M61, M62, M63, M64, M65, M66, M67, M68, M71, M72, M73, M74, M75, M76, M77, M78, M81, M82, M83, M84, M85, M86, M87, M88: HMC5883LSMD; 16LPCC
R1, R2, R3, R4, R5, R6, R7, R8, R9, R10, R11, R12, R13, R14, R15, R16, R17, R18, R19, R20, R21, R22, R23, R24, R25, R26, R27, R28, R29, R30, R31, R32: RESISTOR-ARRAY0603-ARV; 0603-ARV
R33, R34: RESISTOR0603; 0603
SJ1: SOLDERJUMPER_2WAYPASTE1&2; SJ_3_PASTE1&2
U1, U2, U3, U4, U5, U6, U7, U8: TCA9548A; TSSOP-24-4.4MM
U9: MIC5205-3.3YM5; SOT23-5

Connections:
3.3V: C3.1, C6.1, C9.1, C12.1, C15.1, C18.1, C21.1, C24.1, C27.1, C30.1, C33.1, C36.1, C39.1, C42.1, C45.1, C48.1, C51.1, C54.1, C57.1, C60.1, C63.1, C66.1, C69.1, C72.1, C75.1, C78.1, C81.1, C84.1, C87.1, C90.1, C93.1, C96.1, C99.1, C102.1, C105.1, C108.1, C111.1, C114.1, C117.1, C120.1, C123.1, C126.1, C129.1, C132.1, C135.1, C138.1, C141.1, C144.1, C147.1, C150.1, C153.1, C156.1, C159.1, C162.1, C165.1, C168.1, C171.1, C174.1, C177.1, C180.1, C183.1, C186.1, C189.1, C192.1, C194.1, CN1.5, M11.2 (VDD), M11.4 (S1), M11.13 (VDDIO), M12.2 (VDD), M12.4 (S1), M12.13 (VDDIO), M13.2 (VDD), M13.4 (S1), M13.13 (VDDIO), M14.2 (VDD), M14.4 (S1), M14.13 (VDDIO), M15.2 (VDD), M15.4 (S1), M15.13 (VDDIO), M16.2 (VDD), M16.4 (S1), M16.13 (VDDIO), M17.2 (VDD), M17.4 (S1), M17.13 (VDDIO), M18.2 (VDD), M18.4 (S1), M18.13 (VDDIO), M21.2 (VDD), M21.4 (S1), M21.13 (VDDIO), M22.2 (VDD), M22.4 (S1), M22.13 (VDDIO), M23.2 (VDD), M23.4 (S1), M23.13 (VDDIO), M24.2 (VDD), M24.4 (S1), M24.13 (VDDIO), M25.2 (VDD), M25.4 (S1), M25.13 (VDDIO), M26.2 (VDD), M26.4 (S1), M26.13 (VDDIO), M27.2 (VDD), M27.4 (S1), M27.13 (VDDIO), M28.2 (VDD), M28.4 (S1), M28.13 (VDDIO), M31.2 (VDD), M31.4 (S1), M31.13 (VDDIO), M32.2 (VDD), M32.4 (S1), M32.13 (VDDIO), M33.2 (VDD), M33.4 (S1), M33.13 (VDDIO), M34.2 (VDD), M34.4 (S1), M34.13 (VDDIO), M35.2 (VDD), M35.4 (S1), M35.13 (VDDIO), M36.2 (VDD), M36.4 (S1), M36.13 (VDDIO), M37.2 (VDD), M37.4 (S1), M37.13 (VDDIO), M38.2 (VDD), M38.4 (S1), M38.13 (VDDIO), M41.2 (VDD), M41.4 (S1), M41.13 (VDDIO), M42.2 (VDD), M42.4 (S1), M42.13 (VDDIO), M43.2 (VDD), M43.4 (S1), M43.13 (VDDIO), M44.2 (VDD), M44.4 (S1), M44.13 (VDDIO), M45.2 (VDD), M45.4 (S1), M45.13 (VDDIO), M46.2 (VDD), M46.4 (S1), M46.13 (VDDIO), M47.2 (VDD), M47.4 (S1), M47.13 (VDDIO), M48.2 (VDD), M48.4 (S1), M48.13 (VDDIO), M51.2 (VDD), M51.4 (S1), M51.13 (VDDIO), M52.2 (VDD), M52.4 (S1), M52.13 (VDDIO), M53.2 (VDD), M53.4 (S1), M53.13 (VDDIO), M54.2 (VDD), M54.4 (S1), M54.13 (VDDIO), M55.2 (VDD), M55.4 (S1), M55.13 (VDDIO), M56.2 (VDD), M56.4 (S1), M56.13 (VDDIO), M57.2 (VDD), M57.4 (S1), M57.13 (VDDIO), M58.2 (VDD), M58.4 (S1), M58.13 (VDDIO), M61.2 (VDD), M61.4 (S1), M61.13 (VDDIO), M62.2 (VDD), M62.4 (S1), M62.13 (VDDIO), M63.2 (VDD), M63.4 (S1), M63.13 (VDDIO), M64.2 (VDD), M64.4 (S1), M64.13 (VDDIO), M65.2 (VDD), M65.4 (S1), M65.13 (VDDIO), M66.2 (VDD), M66.4 (S1), M66.13 (VDDIO), M67.2 (VDD), M67.4 (S1), M67.13 (VDDIO), M68.2 (VDD), M68.4 (S1), M68.13 (VDDIO), M71.2 (VDD), M71.4 (S1), M71.13 (VDDIO), M72.2 (VDD), M72.4 (S1)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
5V: CN1.6, SJ1.1, U9.1 (IN), U9.3 (EN)
GND: C1.2, C3.2, C4.2, C6.2, C7.2, C9.2, C10.2, C12.2, C13.2, C15.2, C16.2, C18.2, C19.2, C21.2, C22.2, C24.2, C25.2, C27.2, C28.2, C30.2, C31.2, C33.2, C34.2, C36.2, C37.2, C39.2, C40.2, C42.2, C43.2, C45.2, C46.2, C48.2, C49.2, C51.2, C52.2, C54.2, C55.2, C57.2, C58.2, C60.2, C61.2, C63.2, C64.2, C66.2, C67.2, C69.2, C70.2, C72.2, C73.2, C75.2, C76.2, C78.2, C79.2, C81.2, C82.2, C84.2, C85.2, C87.2, C88.2, C90.2, C91.2, C93.2, C94.2, C96.2, C97.2, C99.2, C100.2, C102.2, C103.2, C105.2, C106.2, C108.2, C109.2, C111.2, C112.2, C114.2, C115.2, C117.2, C118.2, C120.2, C121.2, C123.2, C124.2, C126.2, C127.2, C129.2, C130.2, C132.2, C133.2, C135.2, C136.2, C138.2, C139.2, C141.2, C142.2, C144.2, C145.2, C147.2, C148.2, C150.2, C151.2, C153.2, C154.2, C156.2, C157.2, C159.2, C160.2, C162.2, C163.2, C165.2, C166.2, C168.2, C169.2, C171.2, C172.2, C174.2, C175.2, C177.2, C178.2, C180.2, C181.2, C183.2, C184.2, C186.2, C187.2, C189.2, C190.2, C192.2, C193.2, C194.2, CN1.1, M11.9 (GND), M11.11 (GND), M12.9 (GND), M12.11 (GND), M13.9 (GND), M13.11 (GND), M14.9 (GND), M14.11 (GND), M15.9 (GND), M15.11 (GND), M16.9 (GND), M16.11 (GND), M17.9 (GND), M17.11 (GND), M18.9 (GND), M18.11 (GND), M21.9 (GND), M21.11 (GND), M22.9 (GND), M22.11 (GND), M23.9 (GND), M23.11 (GND), M24.9 (GND), M24.11 (GND), M25.9 (GND), M25.11 (GND), M26.9 (GND), M26.11 (GND), M27.9 (GND), M27.11 (GND), M28.9 (GND), M28.11 (GND), M31.9 (GND), M31.11 (GND), M32.9 (GND), M32.11 (GND), M33.9 (GND), M33.11 (GND), M34.9 (GND), M34.11 (GND), M35.9 (GND), M35.11 (GND), M36.9 (GND), M36.11 (GND), M37.9 (GND), M37.11 (GND), M38.9 (GND), M38.11 (GND), M41.9 (GND), M41.11 (GND), M42.9 (GND), M42.11 (GND), M43.9 (GND), M43.11 (GND), M44.9 (GND), M44.11 (GND), M45.9 (GND), M45.11 (GND), M46.9 (GND), M46.11 (GND), M47.9 (GND), M47.11 (GND), M48.9 (GND), M48.11 (GND), M51.9 (GND), M51.11 (GND), M52.9 (GND), M52.11 (GND), M53.9 (GND), M53.11 (GND), M54.9 (GND), M54.11 (GND), M55.9 (GND), M55.11 (GND), M56.9 (GND), M56.11 (GND), M57.9 (GND), M57.11 (GND), M58.9 (GND), M58.11 (GND), M61.9 (GND), M61.11 (GND), M62.9 (GND), M62.11 (GND)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
unnamed: C4.1, M12.10 (C1)
unnamed: C5.1, M12.12 (SETC)
unnamed: C5.2, M12.8 (SETP)
unnamed: C7.1, M13.10 (C1)
unnamed: C8.1, M13.12 (SETC)
unnamed: C1.1, M11.10 (C1)
unnamed: C8.2, M13.8 (SETP)
unnamed: C10.1, M14.10 (C1)
unnamed: C2.1, M11.12 (SETC)
unnamed: C2.2, M11.8 (SETP)
unnamed: C11.1, M14.12 (SETC)
unnamed: C11.2, M14.8 (SETP)
unnamed: C13.1, M15.10 (C1)
unnamed: C14.1, M15.12 (SETC)
unnamed: C14.2, M15.8 (SETP)
unnamed: C16.1, M16.10 (C1)
unnamed: C17.1, M16.12 (SETC)
unnamed: C17.2, M16.8 (SETP)
unnamed: C19.1, M17.10 (C1)
unnamed: C20.1, M17.12 (SETC)
unnamed: C20.2, M17.8 (SETP)
unnamed: C22.1, M18.10 (C1)
unnamed: C23.1, M18.12 (SETC)
unnamed: C23.2, M18.8 (SETP)
unnamed: C25.1, M21.10 (C1)
unnamed: C26.1, M21.12 (SETC)
unnamed: C26.2, M21.8 (SETP)
unnamed: C28.1, M22.10 (C1)
unnamed: C29.1, M22.12 (SETC)
unnamed: C29.2, M22.8 (SETP)
unnamed: C31.1, M23.10 (C1)
unnamed: C32.1, M23.12 (SETC)
unnamed: C32.2, M23.8 (SETP)
unnamed: C34.1, M24.10 (C1)
unnamed: C35.1, M24.12 (SETC)
unnamed: C35.2, M24.8 (SETP)
unnamed: C37.1, M25.10 (C1)
unnamed: C38.1, M25.12 (SETC)
unnamed: C38.2, M25.8 (SETP)
unnamed: C40.1, M26.10 (C1)
unnamed: C41.1, M26.12 (SETC)
unnamed: C41.2, M26.8 (SETP)
unnamed: C43.1, M27.10 (C1)
unnamed: C44.1, M27.12 (SETC)
unnamed: C44.2, M27.8 (SETP)
unnamed: C46.1, M28.10 (C1)
unnamed: C47.1, M28.12 (SETC)
unnamed: C47.2, M28.8 (SETP)
unnamed: C49.1, M31.10 (C1)
unnamed: C50.1, M31.12 (SETC)
unnamed: C50.2, M31.8 (SETP)
unnamed: C52.1, M32.10 (C1)
unnamed: C53.1, M32.12 (SETC)
unnamed: C53.2, M32.8 (SETP)
unnamed: C55.1, M33.10 (C1)
unnamed: C56.1, M33.12 (SETC)
unnamed: C56.2, M33.8 (SETP)
unnamed: C58.1, M34.10 (C1)
unnamed: C59.1, M34.12 (SETC)
unnamed: C59.2, M34.8 (SETP)
unnamed: C61.1, M35.10 (C1)
unnamed: C62.1, M35.12 (SETC)
unnamed: C62.2, M35.8 (SETP)
unnamed: C64.1, M36.10 (C1)
unnamed: C65.1, M36.12 (SETC)
unnamed: C65.2, M36.8 (SETP)
unnamed: C67.1, M37.10 (C1)
unnamed: C68.1, M37.12 (SETC)
unnamed: C68.2, M37.8 (SETP)
unnamed: C70.1, M38.10 (C1)
unnamed: C71.1, M38.12 (SETC)
unnamed: C71.2, M38.8 (SETP)
unnamed: C73.1, M41.10 (C1)
unnamed: C74.1, M41.12 (SETC)
unnamed: C74.2, M41.8 (SETP)
unnamed: C76.1, M42.10 (C1)
unnamed: C77.1, M42.12 (SETC)
unnamed: C77.2, M42.8 (SETP)
unnamed: C79.1, M43.10 (C1)
unnamed: C80.1, M43.12 (SETC)
unnamed: C80.2, M43.8 (SETP)
unnamed: C82.1, M44.10 (C1)
unnamed: C83.1, M44.12 (SETC)
unnamed: C83.2, M44.8 (SETP)
unnamed: C85.1, M45.10 (C1)
unnamed: C86.1, M45.12 (SETC)
unnamed: C86.2, M45.8 (SETP)
unnamed: C88.1, M46.10 (C1)
unnamed: C89.1, M46.12 (SETC)
unnamed: C89.2, M46.8 (SETP)
unnamed: C91.1, M47.10 (C1)
unnamed: C92.1, M47.12 (SETC)
unnamed: C92.2, M47.8 (SETP)
unnamed: C94.1, M48.10 (C1)
unnamed: C95.1, M48.12 (SETC)
unnamed: C95.2, M48.8 (SETP)
unnamed: C97.1, M51.10 (C1)
unnamed: C98.1, M51.12 (SETC)
unnamed: C98.2, M51.8 (SETP)
unnamed: C100.1, M52.10 (C1)
unnamed: C101.1, M52.12 (SETC)
unnamed: C101.2, M52.8 (SETP)
unnamed: C103.1, M53.10 (C1)
unnamed: C104.1, M53.12 (SETC)
unnamed: C104.2, M53.8 (SETP)
unnamed: C106.1, M54.10 (C1)
unnamed: C107.1, M54.12 (SETC)
unnamed: C107.2, M54.8 (SETP)
unnamed: C109.1, M55.10 (C1)
unnamed: C110.1, M55.12 (SETC)
unnamed: C110.2, M55.8 (SETP)
unnamed: C112.1, M56.10 (C1)
unnamed: C113.1, M56.12 (SETC)
unnamed: C113.2, M56.8 (SETP)
unnamed: C115.1, M57.10 (C1)
unnamed: C116.1, M57.12 (SETC)
unnamed: C116.2, M57.8 (SETP)
unnamed: C118.1, M58.10 (C1)
unnamed: C119.1, M58.12 (SETC)
unnamed: C119.2, M58.8 (SETP)
unnamed: C121.1, M61.10 (C1)
unnamed: C122.1, M61.12 (SETC)
unnamed: C122.2, M61.8 (SETP)
unnamed: C124.1, M62.10 (C1)
unnamed: C125.1, M62.12 (SETC)
unnamed: C125.2, M62.8 (SETP)
unnamed: C127.1, M63.10 (C1)
unnamed: C128.1, M63.12 (SETC)
unnamed: C128.2, M63.8 (SETP)
unnamed: C130.1, M64.10 (C1)
unnamed: C131.1, M64.12 (SETC)
unnamed: C131.2, M64.8 (SETP)
unnamed: C133.1, M65.10 (C1)
unnamed: C134.1, M65.12 (SETC)
unnamed: C134.2, M65.8 (SETP)
unnamed: C136.1, M66.10 (C1)
unnamed: C137.1, M66.12 (SETC)
unnamed: C137.2, M66.8 (SETP)
unnamed: C139.1, M67.10 (C1)
unnamed: C140.1, M67.12 (SETC)
unnamed: C140.2, M67.8 (SETP)
unnamed: C142.1, M68.10 (C1)
unnamed: C143.1, M68.12 (SETC)
unnamed: C143.2, M68.8 (SETP)
unnamed: C145.1, M71.10 (C1)
unnamed: C146.1, M71.12 (SETC)
unnamed: C146.2, M71.8 (SETP)
unnamed: C148.1, M72.10 (C1)
unnamed: C149.1, M72.12 (SETC)
unnamed: C149.2, M72.8 (SETP)
unnamed: C151.1, M73.10 (C1)
unnamed: C152.1, M73.12 (SETC)
unnamed: C152.2, M73.8 (SETP)
unnamed: C154.1, M74.10 (C1)
unnamed: C155.1, M74.12 (SETC)
unnamed: C155.2, M74.8 (SETP)
unnamed: C157.1, M75.10 (C1)
unnamed: C158.1, M75.12 (SETC)
unnamed: C158.2, M75.8 (SETP)
unnamed: C160.1, M76.10 (C1)
unnamed: C161.1, M76.12 (SETC)
unnamed: C161.2, M76.8 (SETP)
unnamed: C163.1, M77.10 (C1)
unnamed: C164.1, M77.12 (SETC)
unnamed: C164.2, M77.8 (SETP)
unnamed: C166.1, M78.10 (C1)
unnamed: C167.1, M78.12 (SETC)
unnamed: C167.2, M78.8 (SETP)
unnamed: C169.1, M81.10 (C1)
unnamed: C170.1, M81.12 (SETC)
unnamed: C170.2, M81.8 (SETP)
unnamed: C172.1, M82.10 (C1)
unnamed: C173.1, M82.12 (SETC)
unnamed: C173.2, M82.8 (SETP)
unnamed: C175.1, M83.10 (C1)
unnamed: C176.1, M83.12 (SETC)
unnamed: C176.2, M83.8 (SETP)
unnamed: C178.1, M84.10 (C1)
unnamed: C179.1, M84.12 (SETC)
unnamed: C179.2, M84.8 (SETP)
unnamed: C181.1, M85.10 (C1)
unnamed: C182.1, M85.12 (SETC)
unnamed: C182.2, M85.8 (SETP)
unnamed: C184.1, M86.10 (C1)
unnamed: C185.1, M86.12 (SETC)
unnamed: C185.2, M86.8 (SETP)
unnamed: C187.1, M87.10 (C1)
unnamed: C188.1, M87.12 (SETC)
unnamed: C188.2, M87.8 (SETP)
unnamed: C190.1, M88.10 (C1)
unnamed: C191.1, M88.12 (SETC)
unnamed: C191.2, M88.8 (SETP)
unnamed: C193.1, U9.4 (BP)
unnamed: R33.2, R34.2, SJ1.2
RESET: CN1.4, U1.3 (RST#), U2.3 (RST#), U3.3 (RST#), U4.3 (RST#), U5.3 (RST#), U6.3 (RST#), U7.3 (RST#), U8.3 (RST#)
SCL: CN1.2, R34.1, U1.22 (SCL), U2.22 (SCL), U3.22 (SCL), U4.22 (SCL), U5.22 (SCL), U6.22 (SCL), U7.22 (SCL), U8.22 (SCL)
SCL11: M11.1 (SCL), R3.5 (2), U1.20 (SCL7)
SCL12: M12.1 (SCL), R3.7 (2), U1.18 (SCL6)
SCL13: M13.1 (SCL), R4.5 (2), U1.16 (SCL5)
SCL14: M14.1 (SCL), R4.7 (2), U1.14 (SCL4)
SCL15: M15.1 (SCL), R1.3 (1), U1.5 (SCL0)
SCL16: M16.1 (SCL), R1.1, U1.7 (SCL1)
SCL17: M17.1 (SCL), R2.3 (1), U1.9 (SCL2)
SCL18: M18.1 (SCL), R2.1, U1.11 (SCL3)
SCL21: M21.1 (SCL), R7.5 (2), U2.20 (SCL7)
SCL22: M22.1 (SCL), R7.7 (2), U2.18 (SCL6)
SCL23: M23.1 (SCL), R8.5 (2), U2.16 (SCL5)
SCL24: M24.1 (SCL), R8.7 (2), U2.14 (SCL4)
SCL25: M25.1 (SCL), R5.3 (1), U2.5 (SCL0)
SCL26: M26.1 (SCL), R5.1, U2.7 (SCL1)
SCL27: M27.1 (SCL), R6.3 (1), U2.9 (SCL2)
SCL28: M28.1 (SCL), R6.1, U2.11 (SCL3)
SCL31: M31.1 (SCL), R11.5 (2), U3.20 (SCL7)
SCL32: M32.1 (SCL), R11.7 (2), U3.18 (SCL6)
SCL33: M33.1 (SCL), R12.5 (2), U3.16 (SCL5)
SCL34: M34.1 (SCL), R12.7 (2), U3.14 (SCL4)
SCL35: M35.1 (SCL), R9.3 (1), U3.5 (SCL0)
SCL36: M36.1 (SCL), R9.1, U3.7 (SCL1)
SCL37: M37.1 (SCL), R10.3 (1), U3.9 (SCL2)
SCL38: M38.1 (SCL), R10.1, U3.11 (SCL3)
SCL41: M41.1 (SCL), R15.5 (2), U4.20 (SCL7)
SCL42: M42.1 (SCL), R15.7 (2), U4.18 (SCL6)
SCL43: M43.1 (SCL), R16.5 (2), U4.16 (SCL5)
SCL44: M44.1 (SCL), R16.7 (2), U4.14 (SCL4)
SCL45: M45.1 (SCL), R13.3 (1), U4.5 (SCL0)
SCL46: M46.1 (SCL), R13.1, U4.7 (SCL1)
SCL47: M47.1 (SCL), R14.3 (1), U4.9 (SCL2)
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

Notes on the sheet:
(I2C_ADDR: 0x1E)
3.3V REGULATOR

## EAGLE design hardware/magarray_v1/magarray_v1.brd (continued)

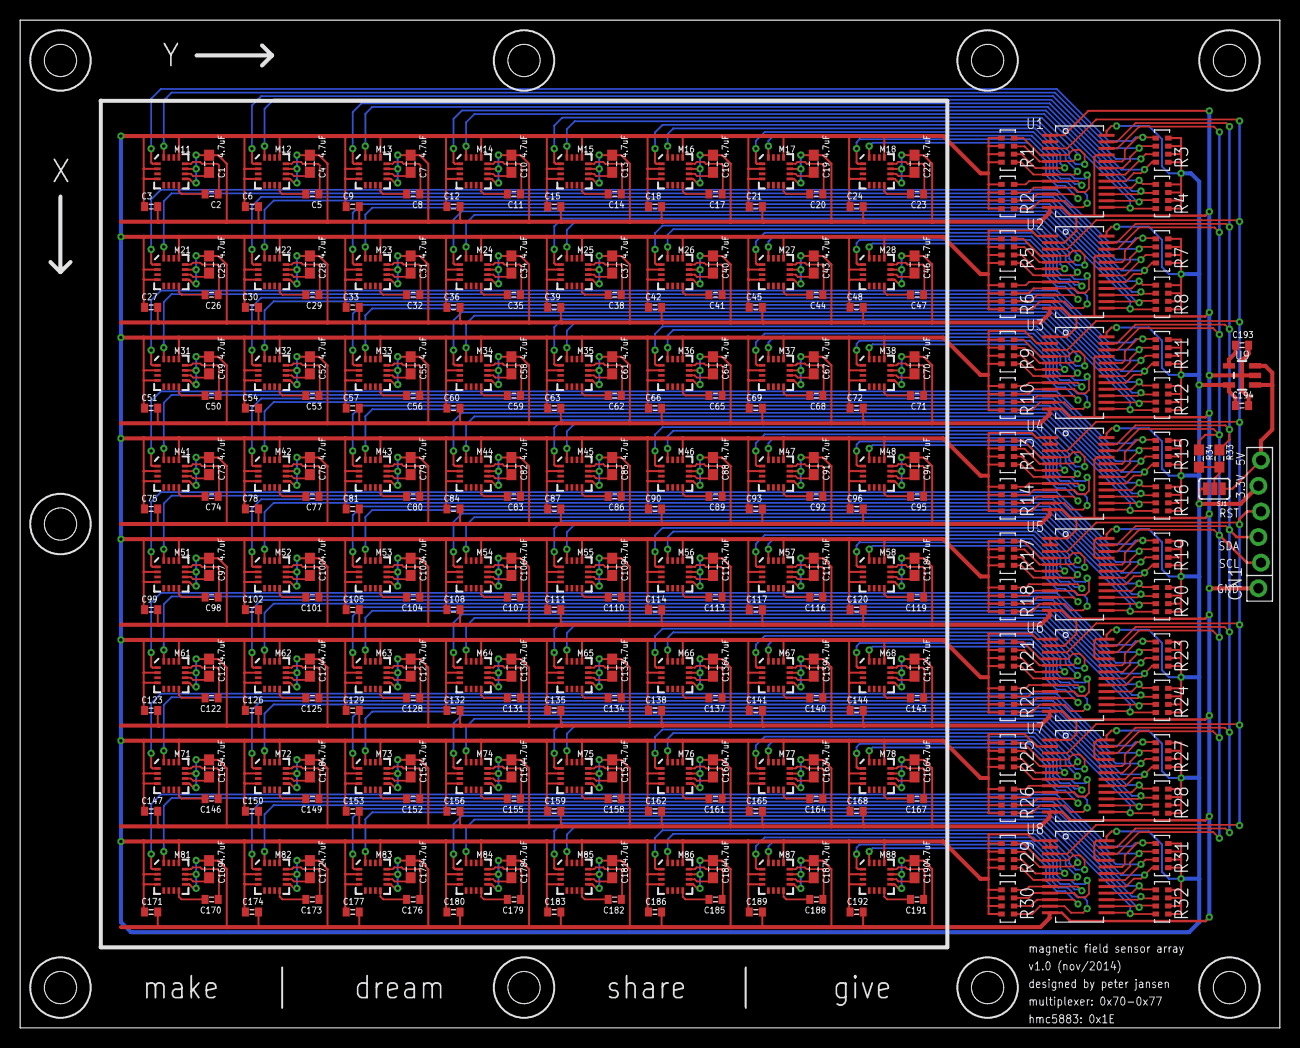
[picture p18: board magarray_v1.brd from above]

Board: 2 copper layers, 125.0 x 100.0 mm, 303 parts (0 on the bottom side), 328 nets.

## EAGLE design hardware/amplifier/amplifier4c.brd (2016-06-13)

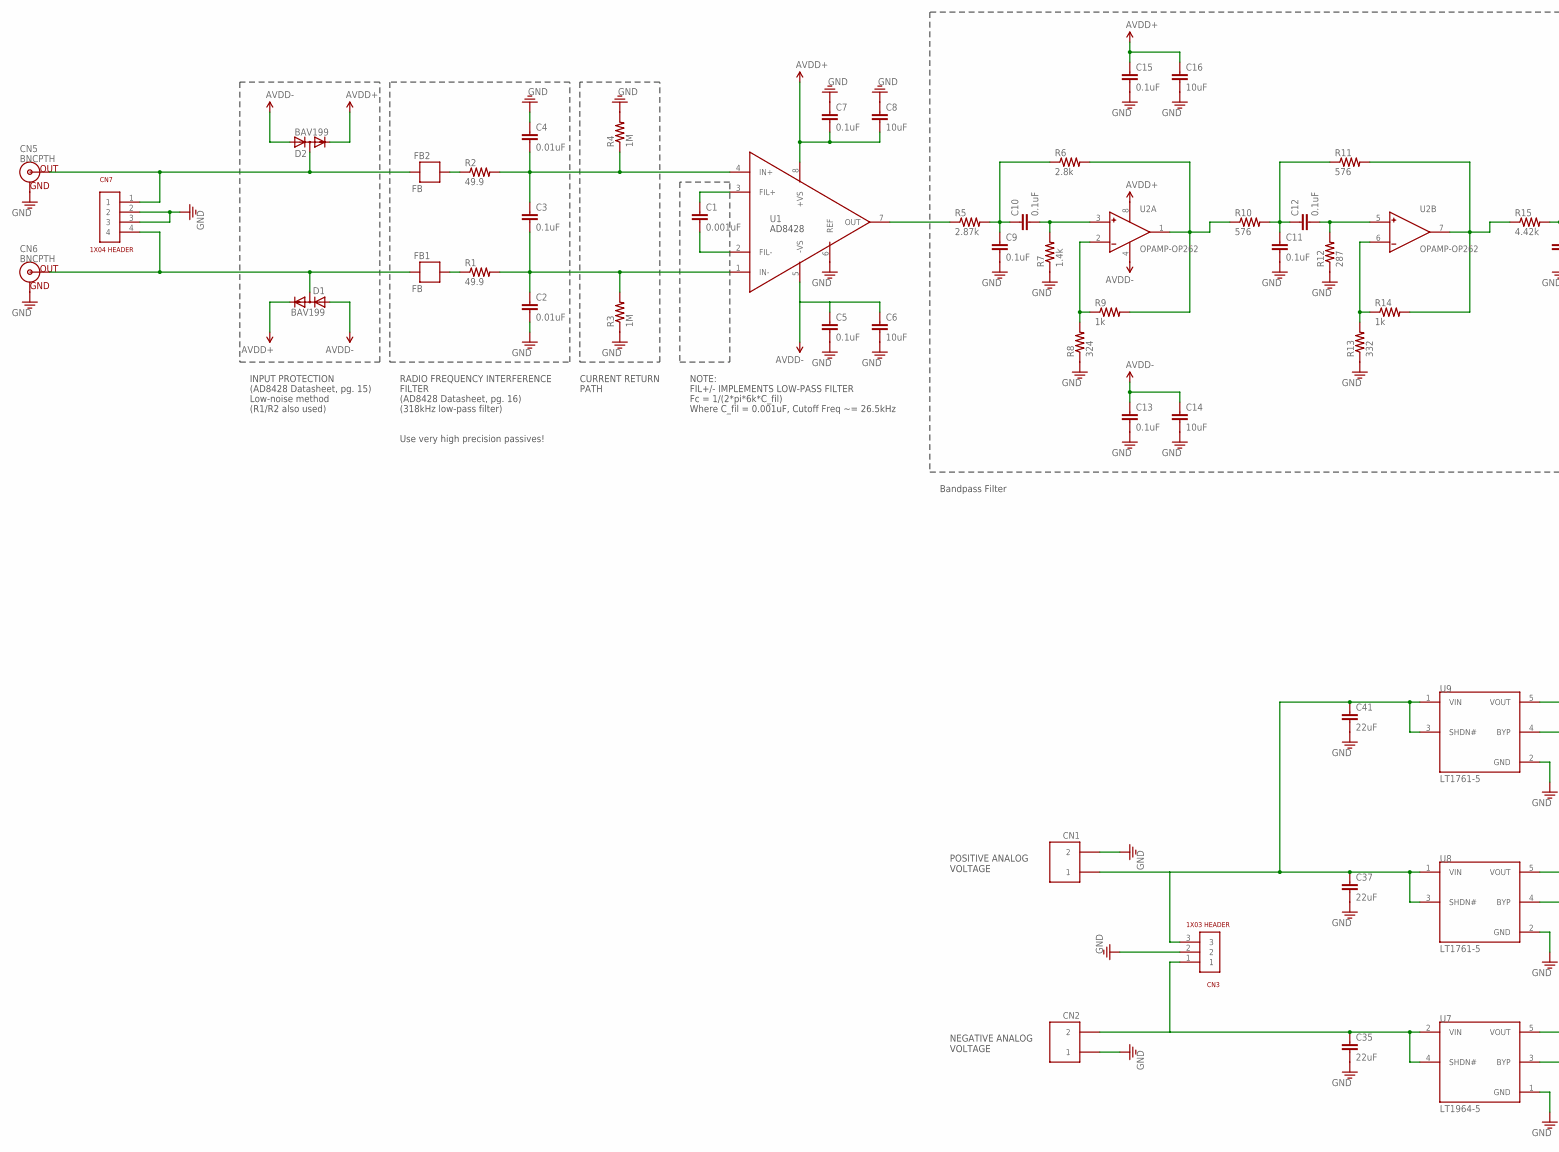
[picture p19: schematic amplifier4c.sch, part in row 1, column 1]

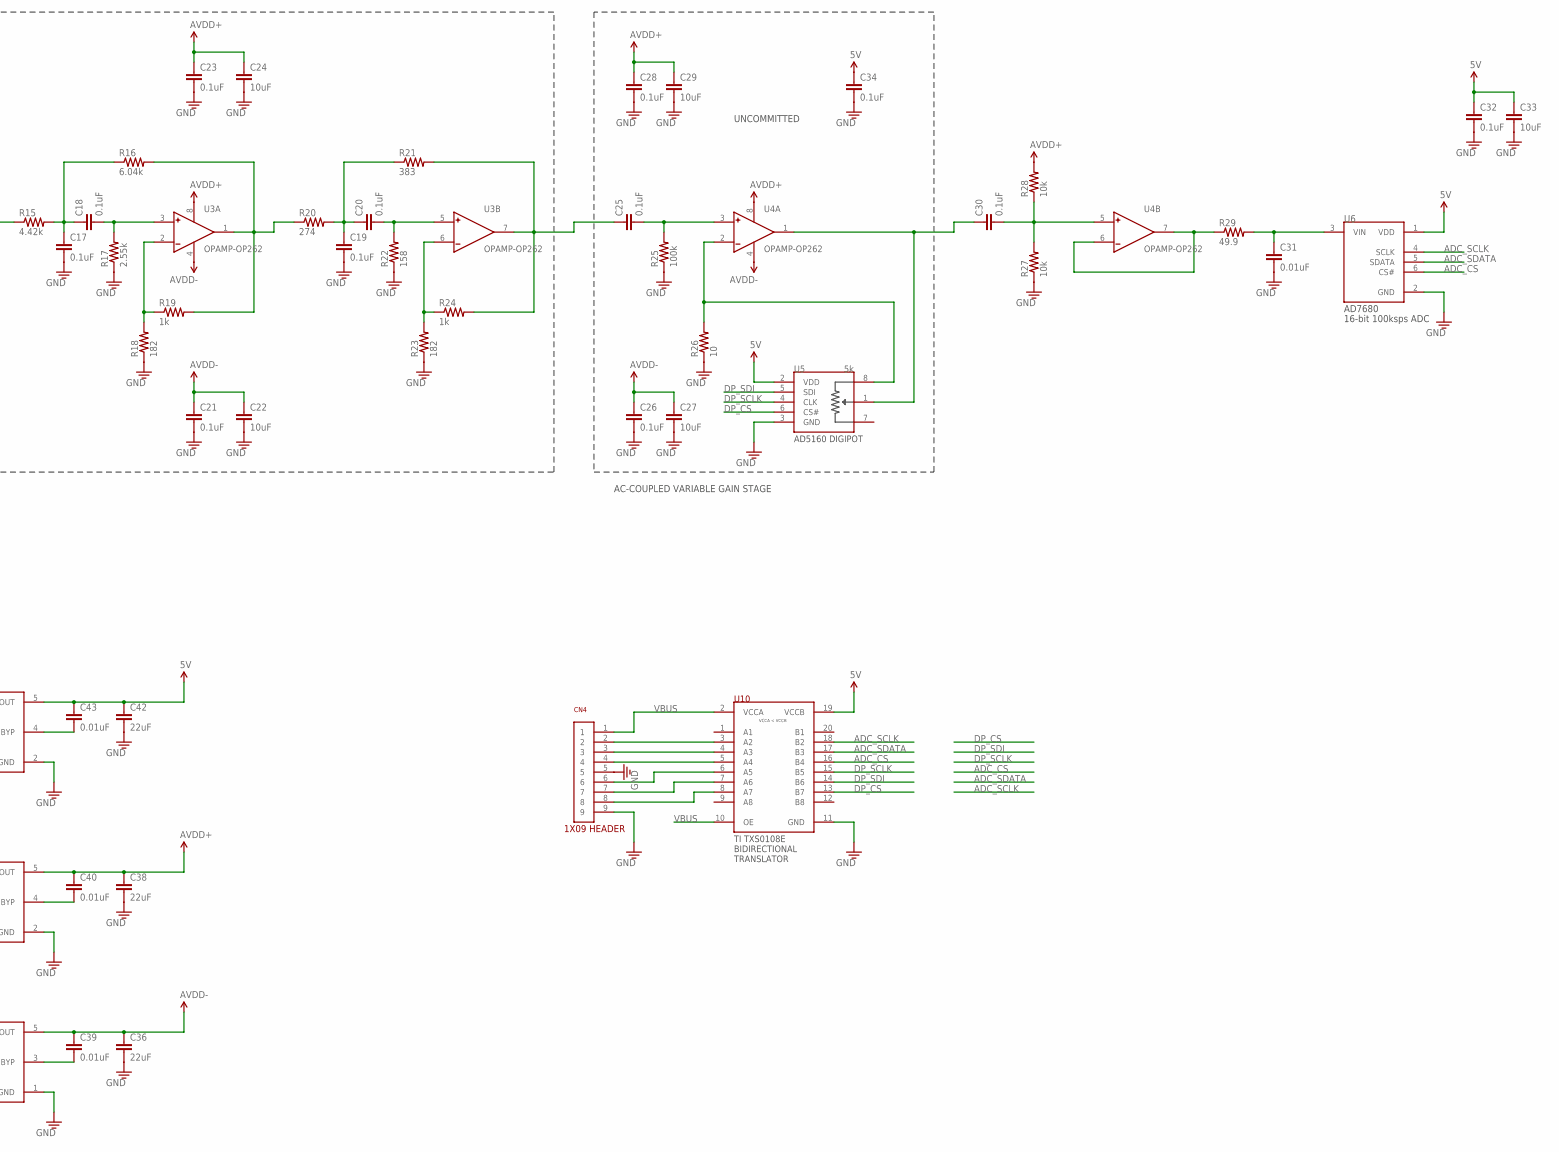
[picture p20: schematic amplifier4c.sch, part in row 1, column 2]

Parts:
C1: 0.001uF; 0603
C2, C4, C31, C39, C40, C43: 0.01uF; 0603
C3, C5, C7, C9, C10, C11, C12, C13, C15, C17, C18, C19, C20, C21, C23, C25, C26, C28, C30, C32, C34: 0.1uF; 0603
C6, C8, C14, C16, C22, C24, C27, C29, C33: 10uF; 0805
C35, C36, C37, C38, C41, C42: 22uF; 1206
CN1, CN2: SCREWTERMINAL-2PIN
CN3: 1X03
CN4: 1X09
CN5, CN6: BNCPTH; BNC
CN7: 1X04
D1, D2: BAV199; SOT23
FB1, FB2: FB; 0603
R1, R2, R29: 49.9; 0603
R3, R4: 1M; 0603
R5: 2.87k; 0603
R6: 2.8k; 0603
R7: 1.4k; 0603
R8: 324; 0603
R9, R14, R19, R24: 1k; 0603
R10, R11: 576; 0603
R12: 287; 0603
R13: 332; 0603
R15: 4.42k; 0603
R16: 6.04k; 0603
R17: 2.55k; 0603
R18, R23: 182; 0603
R20: 274; 0603
R21: 383; 0603
R22: 158; 0603
R25: 100k; 0603
R26: 10; 0603
R27, R28: 10k; 0603
U1: OPAMP-AD8428; SOIC-8
U2, U3, U4: OPAMP-OP262; SOIC-8
U5: 5k; SOT-23-8
U6: ADC-AD7680; SOT-23-6L
U7: LT1964-5; SOT-23-5L
U8, U9: LT1761-5; SOT-23-5L
U10: TRANSLATOR-TXS0108E; TSSOP-20

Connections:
5V: C32.1, C33.1, C34.1, C42.1, C43.1, U5.2 (VDD), U6.1 (VDD), U9.5 (VOUT), U10.19 (VCCB)
ADC_CS: U6.6 (CS#), U10.16 (B4)
ADC_SCLK: U6.4 (SCLK), U10.18 (B2)
ADC_SDATA: U6.5 (SDATA), U10.17 (B3)
AVDD+: C7.2, C8.2, C15.1, C16.1, C23.1, C24.1, C28.1, C29.1, C38.1, C40.1, D1.2 (C), D2.2 (C), R28.2, U1.8 (+VS), U2.8 (V+), U3.8 (V+), U4.8 (V+), U8.5 (VOUT)
AVDD-: C5.1, C6.1, C13.1, C14.1, C21.1, C22.1, C26.1, C27.1, C36.1, C39.1, D1.1 (A), D2.1 (A), U1.5 (-VS), U2.4 (V-), U3.4 (V-), U4.4 (V-), U7.5 (VOUT)
DP_CS: U5.6 (CS#), U10.13 (B7)
DP_SCLK: U5.4 (CLK), U10.15 (B5)
DP_SDI: U5.5 (SDI), U10.14 (B6)
GND: C2.2, C4.1, C5.2, C6.2, C7.1, C8.1, C9.2, C11.2, C13.2, C14.2, C15.2, C16.2, C17.2, C19.2, C21.2, C22.2, C23.2, C24.2, C26.2, C27.2, C28.2, C29.2, C31.2, C32.2, C33.2, C34.2, C35.2, C36.2, C37.2, C38.2, C41.2, C42.2, CN1.2, CN2.1, CN3.2, CN4.5, CN4.9, CN5.GND, CN6.GND, CN7.2, CN7.3, R3.1, R4.2, R7.1, R8.1, R12.1, R13.1, R17.1, R18.1, R22.1, R23.1, R25.1, R26.1, R27.1, U1.6 (REF), U5.3 (GND), U6.2 (GND), U7.1 (GND), U8.2 (GND), U9.2 (GND), U10.11 (GND)
unnamed: C1.1, U1.3 (FIL+)
unnamed: C1.2, U1.2 (FIL-)
unnamed: C3.1, C4.2, R2.2, R4.1, U1.4 (IN+)
unnamed: C2.1, C3.2, R1.2, R3.2, U1.1 (IN-)
unnamed: C9.1, C10.1, R5.2, R6.1
unnamed: FB1.1, R1.1
unnamed: FB2.1, R2.1
unnamed: CN6.S (OUT), CN7.4, D1.3 (AC), FB1.2
unnamed: CN5.S (OUT), CN7.1, D2.3 (AC), FB2.2
unnamed: C10.2, R7.2, U2.3 (+)
unnamed: R8.2, R9.1, U2.2 (-)
unnamed: R5.1, U1.7 (OUT)
unnamed: R6.2, R9.2, R10.1, U2.1 (OUT)
unnamed: C25.2, R25.2, U4.3 (+)
unnamed: C11.1, C12.1, R10.2, R11.1
unnamed: C12.2, R12.2, U2.5 (+)
unnamed: R13.2, R14.1, U2.6 (-)
unnamed: R11.2, R14.2, R15.1, U2.7 (OUT)
unnamed: C17.1, C18.1, R15.2, R16.1
unnamed: C18.2, R17.2, U3.3 (+)
unnamed: R18.2, R19.1, U3.2 (-)
unnamed: R16.2, R19.2, R20.1, U3.1 (OUT)
unnamed: C19.1, C20.1, R20.2, R21.1
unnamed: C20.2, R22.2, U3.5 (+)
unnamed: R23.2, R24.1, U3.6 (-)
unnamed: C25.1, R21.2, R24.2, U3.7 (OUT)
unnamed: R26.2, U4.2 (-), U5.8 (A)
unnamed: C30.1, U4.1 (OUT), U5.1 (W)
unnamed: C31.1, R29.2, U6.3 (VIN)
unnamed: C30.2, R27.2, R28.1, U4.5 (+)
unnamed: R29.1, U4.6 (-), U4.7 (OUT)
unnamed: CN4.2, U10.3 (A2)
unnamed: CN4.3, U10.4 (A3)
unnamed: CN4.4, U10.5 (A4)
unnamed: CN4.6, U10.6 (A5)
unnamed: CN4.7, U10.7 (A6)
unnamed: CN4.8, U10.8 (A7)
unnamed: C40.2, U8.4 (BYP)
unnamed: C43.2, U9.4 (BYP)
unnamed: C39.2, U7.3 (BYP)
VBUS: CN4.1, U10.2 (VCCA), U10.10 (OE)
VIN+: C37.1, C41.1, CN1.1, CN3.3, U8.1 (VIN), U8.3 (SHDN#), U9.1 (VIN), U9.3 (SHDN#)
VIN-: C35.1, CN2.2, CN3.1, U7.2 (VIN), U7.4 (SHDN#)

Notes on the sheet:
FIL+/- IMPLEMENTS LOW-PASS FILTER
Fc = 1/(2*pi*6k*C_fil)
Where C_fil = 0.001uF, Cutoff Freq ~= 26.5kHz
NOTE:
INPUT PROTECTION
(AD8428 Datasheet, pg. 15)
Low-noise method
CURRENT RETURN
PATH
RADIO FREQUENCY INTERFERENCE
FILTER
(R1/R2 also used)
(318kHz low-pass filter)
(AD8428 Datasheet, pg. 16)
Use very high precision passives!
Bandpass Filter
UNCOMMITTED
AC-COUPLED VARIABLE GAIN STAGE
POSITIVE ANALOG VOLTAGE
NEGATIVE ANALOG VOLTAGE

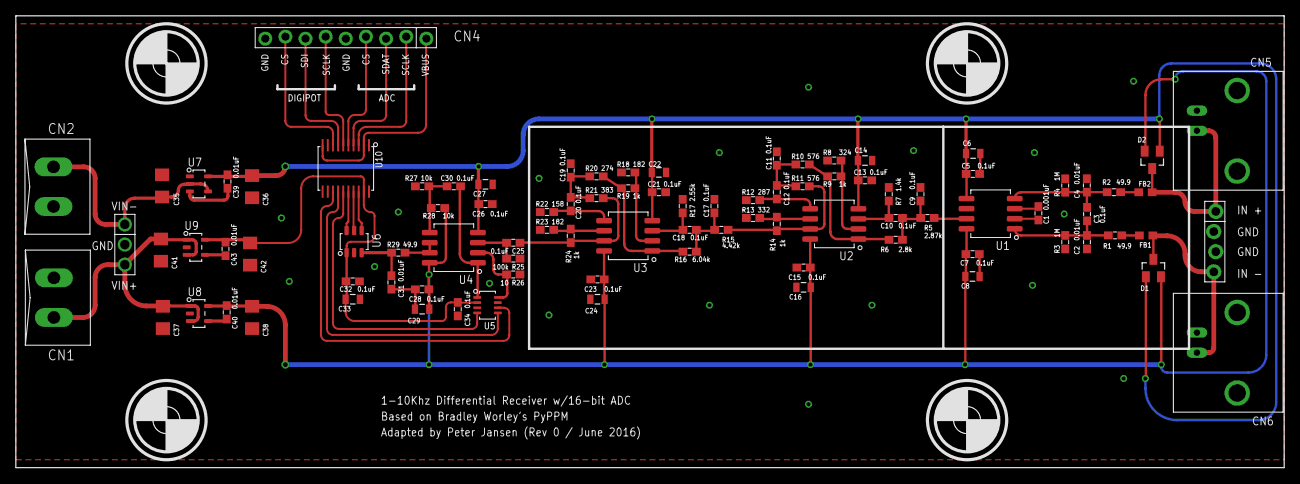
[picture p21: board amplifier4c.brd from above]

Board: 2 copper layers, 160.0 x 57.0 mm, 93 parts (0 on the bottom side), 53 nets.

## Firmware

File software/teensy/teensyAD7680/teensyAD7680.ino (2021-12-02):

// Pins
#define DIGIPOT_CS    3
#define DIGIPOT_MOSI  5
#define DIGIPOT_SCLK  4

#define SPI_CS        53

// AD7680
#define ADC_CS    10
#define ADC_MISO  12
#define ADC_SCK   14

void shortDelay() {
  int a=0; 
  for (int i=0; i<44; i++) {
    __asm__("nop\n\t");
  }
}

uint16_t readAD7680() {
  uint32_t value = 0;  
  
  // Step 1: Activate CS
  digitalWrite(ADC_CS, 0);    
  shortDelay();
  
  for (int i=0; i<23; i++) {
    digitalWrite(ADC_SCK, 0);   // Clock down (data changes)
    // Do nothing
    shortDelay();
    
    digitalWrite(ADC_SCK, 1);   // Clock up (data valid)
    shortDelay();
    // Read bit
    int bitIn = digitalRead(ADC_MISO);
    //Serial.print("BIT: "); Serial.println(bitIn);
    value = value << 1;
    value = value + (bitIn & 0x01);    
  }
  shortDelay();
  // Set bus to idle
  idleAD7680();
  shortDelay();

  value = value >> 4;
  
  return (uint16_t)value;
}

void idleAD7680() {
  digitalWrite(ADC_CS, 1);    
  digitalWrite(ADC_SCK, 1);
}

void setupAD7680() {
  pinMode(ADC_CS, OUTPUT);
  pinMode(ADC_SCK, OUTPUT);
  pinMode(ADC_MISO, INPUT);

  idleAD7680();
}


// Read AD7680 16-bit ADC
uint16_t ReadAD7680() {
  uint8_t sendBuffer[3] = {0, 0, 0};
  uint8_t receiveBuffer[3] = {0, 0, 0};
  
  // Bring SS low to begin the transaction.
  //  spi.setSelect(LOW);
  digitalWrite(SPI_CS, LOW);


  // Delay a short while
  //Delay10us();

  // Clock data from the AD7680.  It takes 3 bytes per conversion. 
  //## spi.transfer(3, sendBuffer, receiveBuffer);
  
  // Bring SS high to end the transaction.
//  spi.setSelect(HIGH);
  digitalWrite(SPI_CS, HIGH);

  // Extract the 16-bit ADC value from the 24-bit buffer.  
  // 4 leading and 4 trailing zeros.    
  uint16_t out = (receiveBuffer[0] << 12) + (receiveBuffer[1] << 4) + (receiveBuffer[2] >> 4);
  /*
  Serial.print(uint16_t(receiveBuffer[0]));
  Serial.print(",");
  Serial.print(uint16_t(receiveBuffer[1]));
  Serial.print(",");
  Serial.print(uint16_t(receiveBuffer[2]));
  Serial.println("");
  */
  return out;
}


//  Delay10us
void Delay10us() {
  volatile int  cnt;
  for (cnt = 0; cnt < 100; cnt++) {
  }
}


/*
 * Digipot
 */ 
void setDigipot(uint8_t value) {
  // Idle
  uint8_t val = value;
  digitalWrite(DIGIPOT_SCLK, 1);
  delay(2);
  digitalWrite(DIGIPOT_CS, 0);  // Active
  delay(2);  
  
  for (int i=0; i<8; i++) {
    digitalWrite(DIGIPOT_SCLK, 0);        // Inactive
    delay(1);
    
    // Data
    if ((val & 0x80) > 0) {
      digitalWrite(DIGIPOT_MOSI, 1);
      //Serial.print("1");
    } else {
      digitalWrite(DIGIPOT_MOSI, 0);
      //Serial.print("0");      
    }
    val = val << 1;
    delay(1);
    
    digitalWrite(DIGIPOT_SCLK, 1);      // Active
    delay(2);
      
  }
  
  digitalWrite(DIGIPOT_SCLK, 0);      // Inactive
  delay(2);
  
  digitalWrite(DIGIPOT_CS, 1);   // Inactive
  // Serial.println("");
}


void setup() {

  // Setup pins for Digipot  
  pinMode(DIGIPOT_CS, OUTPUT);
  pinMode(DIGIPOT_MOSI, OUTPUT);
  pinMode(DIGIPOT_SCLK, OUTPUT);
  
  setupAD7680();
  
  // Serial console
  Serial.begin(115200);
  Serial.println("Initializing...");
  
  Serial.println("before");
  //setDigipot(128);
  //setDigipot(37);
  Serial.println("after");
  setDigipot(255);
}

#define MAX_VALUES 50000
//#define MAX_VALUES 50
int count = 0;
void loop() {
  digitalWrite(35, 0);
  delay(100);
  digitalWrite(35, 1);
  delay(100);  
    
  uint16_t values[MAX_VALUES];
  for (int i=0; i<MAX_VALUES; i++) {  
    // Read ADC
//    values[i] = ReadAD7680();    
    values[i] = readAD7680();    

  }

  Serial.println("DATA:");
  for (int i=0; i<MAX_VALUES; i++) {
    Serial.println(values[i]);    
  }
  //Serial.println("--------");
  //Serial.println(count);
  count += 1;
  //delay(100);
}

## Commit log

2016-06-23 Added HMC5883L magnetometer array board, version 1, from first iteration of the project
    [magarray_v1.brd, magarray_v1.sch]
2016-07-11 Added MLX90393 magnetometer breakout board schematics/board artwork
    [MLX90393_breakout1_long.brd, MLX90393_breakout1_long.sch, MLX90393_breakout1_short.brd, MLX90393_breakout1_short.sch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]
2021-12-01 added teensy test code for radio
2021-12-02 Added working Teensy code, verified with logic analyzer (including fixing digipot bug)

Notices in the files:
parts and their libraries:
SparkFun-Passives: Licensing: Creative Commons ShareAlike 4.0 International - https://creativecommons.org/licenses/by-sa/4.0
